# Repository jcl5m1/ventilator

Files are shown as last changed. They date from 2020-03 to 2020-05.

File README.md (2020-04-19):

Last updated 2020/04/19

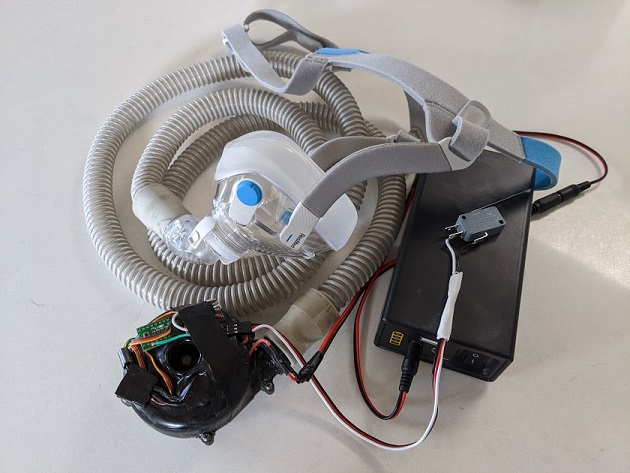
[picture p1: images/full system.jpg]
Full System


# Low-Cost Open-Source Ventilator-ish Device or PAPR

NOTE: This is currently an independent project not affiliated with any commercial institution.

* In the event that COVID-19 hospitalizations exhaust the availability of FDA approved ventilators.  This project documents the process of converting a low-cost CPAP (Continuous Positive Airway Pressure) blower into a rudimentary non-invasive pressure support ventilator that could help with breathing during respiratory distress.  It's an evolving project, but in it's current form, it most aligned with the definition of a non-invasive pressure support BiPAP ventilator.
 * This same project can also be used to create a reasonable [low-cost Powered Air Purifying Respirator (PAPR)](https://github.com/jcl5m1/ventilator/wiki/Build-a-Low-Cost-PAPR) with filter adapter and mask.  PAPRs are effective pieces of Personal Protective Equipment (PPE) that could be helpful to caregivers. PAPRs will also be in extremely short supply and are much less risky and controversial than a DIY ventilator.  You may be able to save many more lives by building a PAPR that protects a caregiver than a mediocre ventilator for one patient.  Unless you are able to participate in the detailed engineering and medical discussions regarding mitigating the risks of high pressure ventilation, I would highly recommend focusing on the PAPR version of this build.

### WARNING/DISCLAIMER: Whenever possible, please seek professional medical care with proper equipment setup by trained individuals. Do not use random information you found on the internet. I am not a medical professional, just a random person putting information on the internet. There are significant risks associated with using a high pressure BiPAP as a DIY ventilator without medical supervision.  

### What are the primary risks of a DIY ventilator?
 * Being viewed as a viable alternative to available professional care or delaying seeking professional care.  This should be viewed as an educational resource or a last resort option only.  Community driven engineering efforts like this run the risk of making it "too easy to be harmful" which would be a bad outcome.
 * Using non-invasive interfaces (such as masks and mouth pieces) can create aerosolized virus infecting many others in clean environments.  Infecing yourself or other healthy individuals multiplies the problem.  Usage should be restricted to places where aerosolized viruses are already abundant (lots of unmasked symptomatic individuals), COVID wards, or in isolation. <strong>NOTE: Self-quarantine in an apartment or multi-unit residence is NOT proper isolation due to potential shared ventilation and sewage.</strong>
* Giving too high a pressure (such as 20cmh2o and up) without observing lung compliance can cause rupture of infected lung tissue.  This design currently lacks several features that provide enough feedback to a caregiver to monitor that risk.
* See [more detailed discussion of these risks and potential engineering/administrative controls to address them](https://github.com/jcl5m1/ventilator/wiki/Notes-from-chatting-with-a-pulmonologist).

### Too risky? Build a low-cost PAPR!
One more time, a [low-cost Powered Air Purifying Respirator (PAPR)](https://github.com/jcl5m1/ventilator/wiki/Build-a-Low-Cost-PAPR) is highly valuable for caregivers, and may have much more positive impact than bulding a mediocre ventilator.

### Want to build something without electronics?  Consider building PPE
* There are many efforts making [DIY face shields](https://www.google.com/search?q=3d+printed+face+shields)
* There are many efforts making [face masks](https://www.google.com/search?q=make%20a%20face%20mask) from home materials.  We've also posted some of [our results of testing filter performance of different materials.](https://github.com/jcl5m1/ventilator/wiki/Material-Filter-Testing)

### Hardware Requirements and Medical/Government Request for proposals:
 * Requirements doc from [Code Life Ventilator Challenge - Montreal General Hospital Foundation](https://www.agorize.com/en/challenges/code-life-challenge/pages/guidelines?lang=en) (Canada)

 * Requirements from [Gov.UK  - Rapidly Manufactured Ventilator System](https://www.gov.uk/government/publications/coronavirus-covid-19-ventilator-supply-specification/rapidly-manufactured-ventilator-system-specification?fbclid=IwAR2IgOyENgHJTsLouIiikpuiwgwupdB8d8Aun2he8nzMPWGfhBVhaG_sMqo) (UK)

### Current Hardware Capabilities
  * This rudimentary design can have a programmable breathing rate (ex: 10-16/min)
  * It can have a programmed Positive End-Expiratory Pressure (PEEP)
  * The blower is physicially able to hit a peak airway pressure of up to 45cmh2o. However, <strong>[going above 20cmh2o can be DANGEROUS](https://github.com/jcl5m1/ventilator/wiki/Notes-from-chatting-with-a-pulmonologist)</strong>.  
  * It cannot yet hit a target tidal volume.  What level of accuracy in volume would be sufficient?  100mL? 10mL?  
  * It does not regulate fractional oxygen (FiO2).  But, a down stream connection to an O2 tank is possible to boost O2 concentration with manual flow adjustment.  I could use a pointer to a low cost O2 sensor.
  * It is lacking in many other ways, but it is possible that this limited functionality could be helpful when better care is not available.  It is also a starting point for making progress.  Critical features can be added over time.

Here's a youtube video walking through the components as of 2020/03/17:
Youtube video (https://www.youtube.com/watch?v=n57u1NvXBgw)

There are also many other efforts in this direction.  [Here's a short list of them](https://github.com/jcl5m1/ventilator/blob/master/resources.md) Thanks! [discussion](https://github.com/jcl5m1/ventilator/pull/20) 

# To Do's - aka Things I could use help with

I've moved the [To Do's to a Wiki](https://github.com/jcl5m1/ventilator/wiki/TaskList) so it is easier to update. Please check there if you are interested in helping.  Thanks to those that already have!

To provide comments/feedback/offer help, [create a new issue](https://github.com/jcl5m1/ventilator/issues) on the project.  Thanks!

# Useful References/Docs about the supply shortages, and guidance around unapproved devices:

There is a growing list of useful documents around guidance for use of unapproved equipment, and information around estimated shortages of both ventilators and personal protective equipment.  We have moved them to [References Wiki to enable better updates](https://github.com/jcl5m1/ventilator/wiki/Useful-References) to make it easier to maintain.

# Materials
1. [Continuous Positive Airway Pressure (CPAP)](https://en.wikipedia.org/wiki/Continuous_positive_airway_pressure) devices are commonly used by individuals to treat [sleep apnea](https://en.wikipedia.org/wiki/Sleep_apnea). As a result, CPAP blower components are fairly abundant. Used ones are available on eBay and new ones on Alibaba. In many of these devices, the blower is a simple BLDC motor that can be driven with an Electronics Speed Controller (ESC) used by quadrotors and RC cars.  The one I used is pulled from a [Respironics REMStar](https://www.google.com/search?q=respironics+remstar&safe=off&rlz=1C1CHBF_enUS809US809&sxsrf=ALeKk00Uw98vXCAyCiiSglgt-2Ucnz5RCg:1584357572342&source=lnms&tbm=isch&sa=X&ved=2ahUKEwj2mq_y757oAhXOvJ4KHV22D1EQ_AUoAnoECAwQBA).  In volume, these blower components can be under $20.  
  * Alternative: test a [12v inflator pump](https://www.amazon.com/gp/product/B013UQ0T2Y/ref=ppx_yo_dt_b_asin_title_o01_s00?ie=UTF8&psc=1) which is even more abundant.  
  * Alternative: [print a blower](https://drmrehorst.blogspot.com/2018/04/the-mother-of-all-print-cooling-fans.html) [[discussion]](https://github.com/jcl5m1/ventilator/issues/8)

2.  [Arduino Compatible Nano/Clone](https://www.amazon.com/s?k=Arduino+nano) to control the motor speed, breathing cycles, and handle user input.   Download the [Arduino IDE](https://www.arduino.cc/en/main/software) to program the [microcontroller software](https://github.com/jcl5m1/ventilator/tree/master/ventilator_control).

3. Brushless DC Motor [Electronic Speed Controller](https://www.amazon.com/Hobbypower-Brushless-Controller-Multicopter-Helicopter/dp/B00XKX5TBE/ref=sr_1_17?keywords=12v+ESC&qid=1584357758&sr=8-17) capable of at least 10A. 

4. Button or switch for input control.  The code cycles through 5 levels of pressure. Double click to switch between CPAP and BiPAP/Fixed PEEP mode.

5. 12v DC power supply that can handle at least 5A.  The blower works pretty hard, and the breathing cycles can create voltage drops which will reset the Arduino if the supply is not strong enough.

6. Tubing and face mask.  If you search for [CPAP face mask](https://www.google.com/search?q=cpap+mask), you'll find many options/suppliers.  A full face mask that covers both the mouth and nose will enable pressure buildup in the lungs.  As an alternative, see below for draft 3D printable parts.

7. Optional [inline 12v battery backup](https://www.amazon.com/gp/product/B07H8F5HYJ/ref=ppx_yo_dt_b_search_asin_title?ie=UTF8&psc=1).

# Building
This is the full system with mask, tubing, pump, 12v battery, and switch for input.  However, I would strongly recommend running this with a DC power supply since the battery will only last about 3-4 hours.  <strong>Wearing the mask with a dead battery could cause dangerous CO2 build up.</strong>  This [particular battery](https://www.amazon.com/gp/product/B07H8F5HYJ/ref=ppx_yo_dt_b_search_asin_title?ie=UTF8&psc=1) can charge and supply power at the same time, acting as an inline battery backup to wall power.

Full System

Below is a close up of the extracted blower.  It is simply a BLDC motor driving a blower fan.  A small ESC and Arduino are attached (technically a Teensy2.0++, but the code has now been changed to an Arduino Nano).  It has a 3d printed tapered hose adpater on it to fit in the hose.  The [microcontroller software](https://github.com/jcl5m1/ventilator/tree/master/ventilator_control) can be programmed with the [Arduino IDE](https://www.arduino.cc/en/main/software). The software goes through a short initialization sequence to configure the ESC; it then starts at the lowest CPAP setting.  You can use the switch to cycle through pressure levels, and double click to cycle through operating modes.

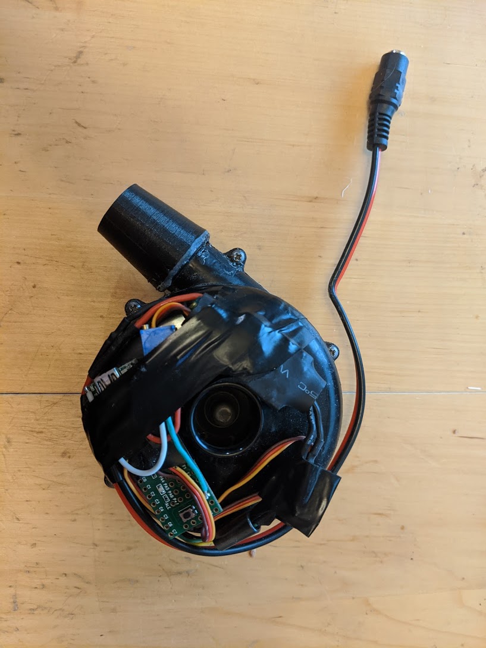
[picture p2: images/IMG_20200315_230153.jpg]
Extracted CPAP Blower


Here is the schematic for the electronics. As you can see, it is very simple with only a few parts.  A slightly modifed version that is able to [sense the blower current is here](https://github.com/jcl5m1/ventilator/wiki/Breathing-Back-Pressure-Data-Analysis).
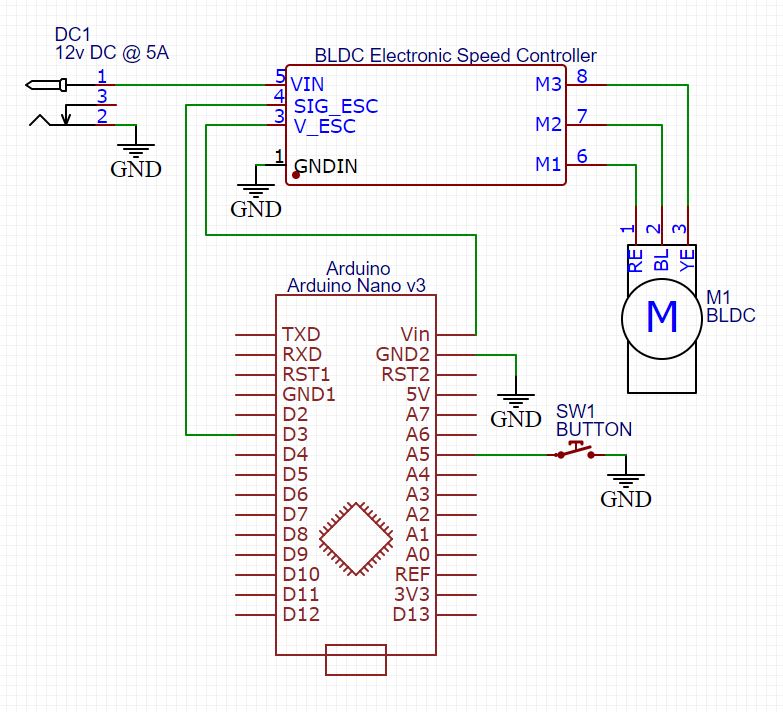
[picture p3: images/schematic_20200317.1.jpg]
schematic


## Face mask / Tube Adapter
Since I have a CPAP, I happen to have a [Resmed AitFit F20](https://www.amazon.com/Resmed-AirFit-Frame-System-Cushion/dp/B07C9MR5RS) mask that I can use.  This is quite comfortable and covers both the nose and mouth to make a good seal.  However, if you can't get a mask,  below is a prototype mouthguard that fits in the category of not-so-great-but-usable-if-you-have-a-lot-of-tape.  I am using some [elastic straps](https://www.amazon.com/gp/product/B07WZRZDPF/ref=ppx_yo_dt_b_search_asin_title?ie=UTF8&psc=1) as head gear.  However, in order to get a good air seal to get enough positive pressure, this would require some tape.  A little bit of leakage is actually desirable to allow CO2 to escape near the mouth and nose to flush out the air over time; this prevents CO2 from being stuck in the tube.  <strong>WARNING: wearing this sealed to the mouth with tape without power may cause dangerous CO2 build up.</strong>

Download the [[3D model]](https://github.com/jcl5m1/ventilator/blob/master/3dmodels/mouthgaurd_v20200316.2.stl) [[Fusion 360 link]](https://a360.co/33rwb1R).

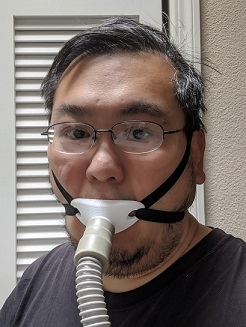
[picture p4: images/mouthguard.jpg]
Mouth Guard

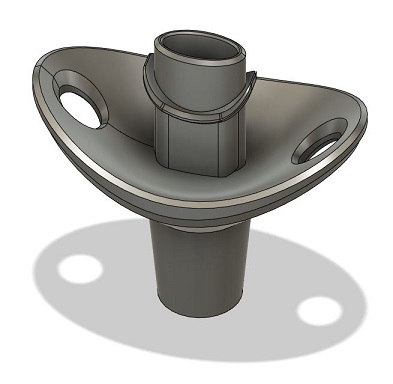
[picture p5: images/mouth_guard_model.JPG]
Mouth Guard model


# Pressure Testing

This is a picture of my test rig to measure the output pressure.  It is a U-shaped tube with an attached measuring tape to check displacement of water.  The actual liquid displacement is 2x the measured line since liquid is being pushed downwards an equal amount on the other side of the U, doubling the displacement. (I think this is the correct way to measure).  At full blast at 12v, it is achieving 45cmh2o. <strong>[WARNING: Going above 20cmh2o can be DANGEROUS](https://github.com/jcl5m1/ventilator/wiki/Notes-from-chatting-with-a-pulmonologist)</strong>.  So, these blowers are plently powerful.

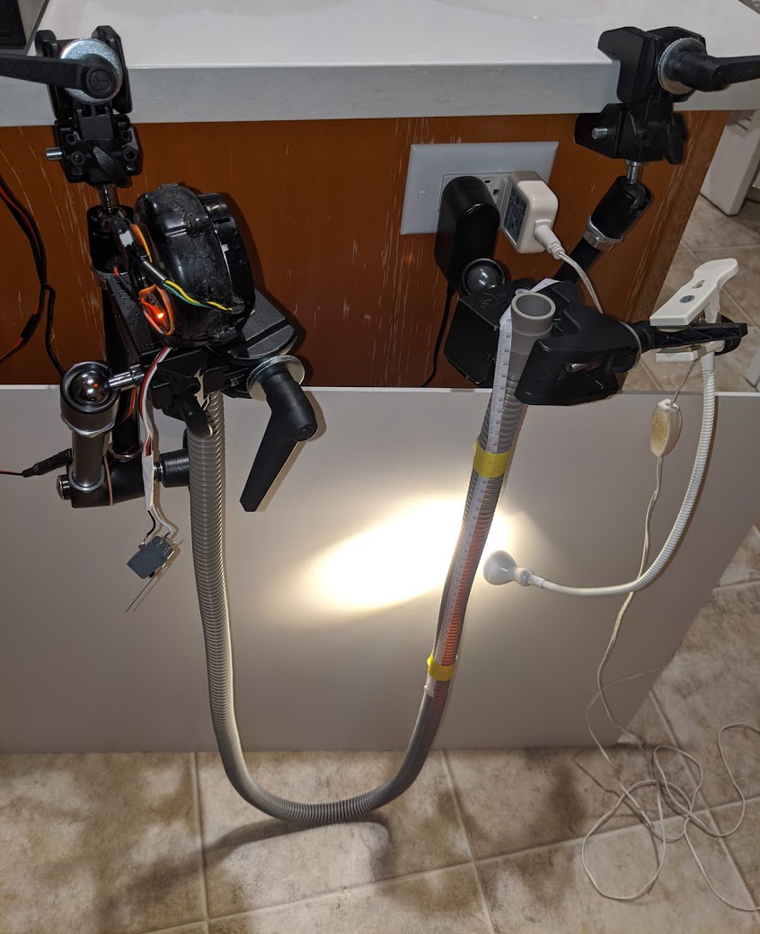
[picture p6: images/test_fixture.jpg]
Pressure measurement fixture


Here are some images showing the dislacement of the liquid at different speeds.  I happen to have Diet Dr. Pepper on hand which makes it easier to see the liquid level rather than just plain water.

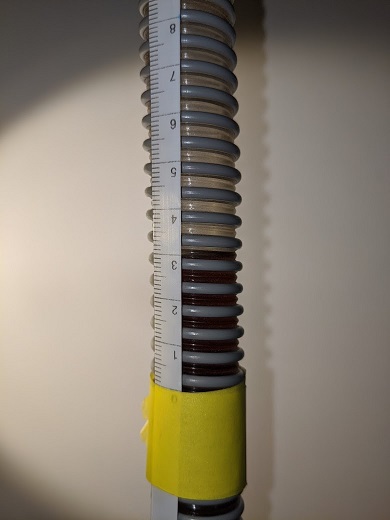
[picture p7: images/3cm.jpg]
3cm
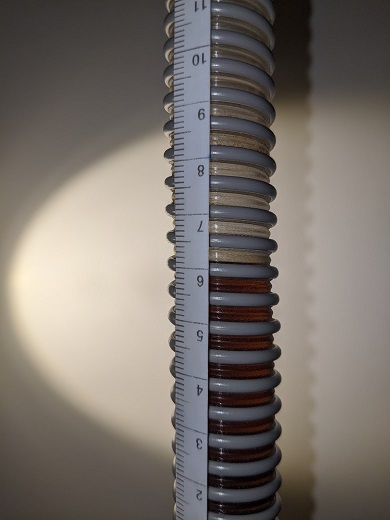
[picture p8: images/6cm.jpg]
6cm
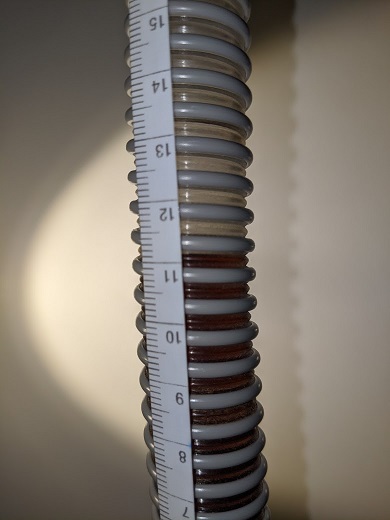
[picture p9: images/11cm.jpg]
11cm
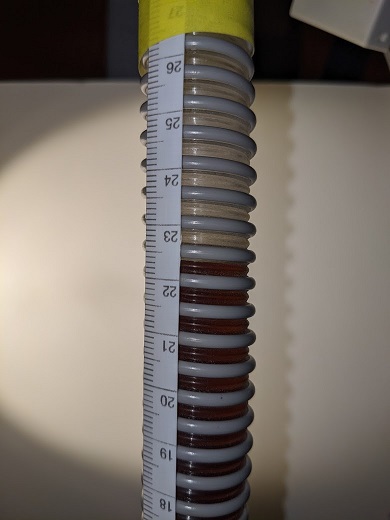
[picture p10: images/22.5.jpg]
22.5cm
   

Here's a [video of the blower pushing a breathing cycle of 16 cycles/min oscilating between 12 and 22cmh2o](https://photos.app.goo.gl/b3yMPE5QpdeduxKS6).

# Air Filtration - PAPR Option

An open air blower into someone's airway isn't great.  If possible, some filtration is preferred.  These parts were originally used for a DIY [Powered Air Purifying Respriator (PAPR)](https://en.wikipedia.org/wiki/Powered_air-purifying_respirator). However, adding a filter will definitely affect the output pressure.  It will depend on the blower you have if the motor can handle the additional load.  Given the headroom of the blower I tested, these CPAP blowers can probably handle the filter and still hit the target pressure.  However, I haven't done long term thermal testing at high pressure and with a strong filter. These adapter plates can be attached with liberal amounts of hot glue and wrapping the unit in vinyl tape to get a reasonably airtight seal.  My blower's enclosure was not air-tight, so it is difficult to guarantee that 100% of the air is coming only through the filter.  Setting the blower to a low CPAP pressure, and leaving the face mask vent holes open will allow it to function reasonably as a PAPR.

* This is an adapter plate for a [3M P100 or N95 face mask filter cartridge](https://www.amazon.com/3M-50051138464658-Cartridge-Filter-Organic/dp/B07571LR2K/ref=sr_1_2?crid=36AKE548EW15U&keywords=3m+p100+cartridge&qid=1584418326&sprefix=3m+p100+cartrige%2Caps%2C202&sr=8-2). Download [[3D model]](https://github.com/jcl5m1/ventilator/blob/master/3dmodels/3M_filter_adapter.stl) [[Fusion 360 link]](https://a360.co/2QnQQOU)

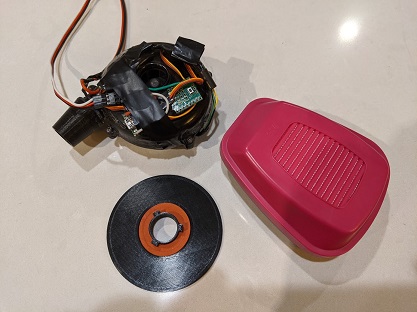
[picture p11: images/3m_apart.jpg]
3M Apart
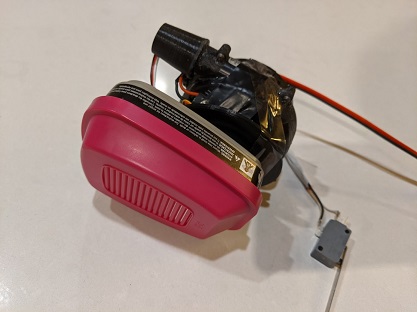
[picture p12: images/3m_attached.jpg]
3M attached
 

* This is an adapter plate for a [NATO 40mm gas mask filter cartridge](https://www.amazon.com/MIRA-Cartridge-Respiratory-Protection-Filter/dp/B07L38TYSF/ref=sr_1_2?keywords=40mm+gas+mask+filters&qid=1584418565&sr=8-2).  These fitlers are available with [CBRN](https://en.wikipedia.org/wiki/CBRN_defense) ratings which are needed for viral and bacterial defense similar to those [approved by the CDC/NIOSH](https://www.cdc.gov/niosh/npptl/standardsdev/cbrn/papr/default.html). Download [[3D model]](https://github.com/jcl5m1/ventilator/blob/master/3dmodels/NATO_40mm_adapter.stl) [[Fusion 360 link]](https://a360.co/3914gXs)

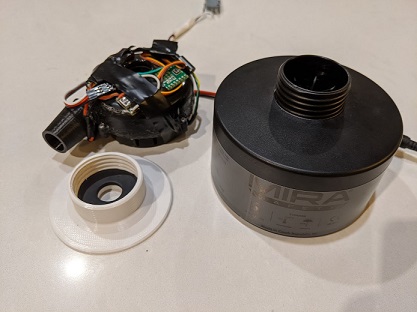
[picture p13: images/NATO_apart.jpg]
NATO Apart
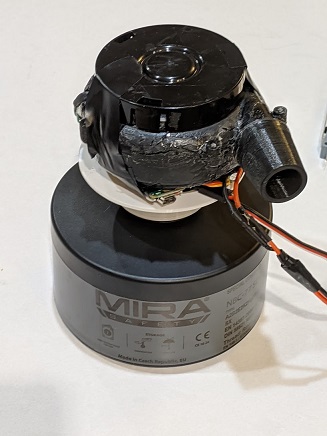
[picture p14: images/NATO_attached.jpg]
NATO attached
 

* This is an option for an [inline filter](https://www.directhomemedical.com/cart/merchant.mvc?Screen=PROD&Product_Code=1-H1605-inline-bacterial-viral-cpap-filters&Store_Code=DHM&gclid=EAIaIQobChMIo-G35omi6AIVSrzACh29hwv3EAQYASABEgK9FPD_BwE) [[discussion]](https://github.com/jcl5m1/ventilator/issues/4) that looks easy to install, and would be helpful for non-CPAP blowers. 

# Update Log

Click [here](https://github.com/jcl5m1/ventilator/wiki) to see updates.

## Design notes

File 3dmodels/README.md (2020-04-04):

# 3D models 

## Requirements & recommendations

**Supported file formats**

- STL - for 3D printed models
- STEP - for objects representing part to be used as a reference
- Application specific projects (like SolidWorks, Fusion360) - CAD formats other users could edit 

**Unsupported file formats**
- Mesh-based objects (.obj, .3dmax, etc) - these formats are not editable by CAD software and should be avoided.

**3D printing recommendations:**

1. Part dimensions should be within 200x200x200mm - print area limits for most 3D printers
2. Avoid overhangs - parts should be printable without Support
3. For bigger parts please also try to provide stacked version - i.e. parts on top of each other, so we could print them in bulk
4. Recommended print settings should be provided for printing with PET-G (material accepted for medical purposes)

# Reference sheet on original parts

## CPAP filter
Please check Wiki page for more details: https://github.com/jcl5m1/ventilator/wiki/Bacterial-Viral-Filter-for-CPAP-Machines

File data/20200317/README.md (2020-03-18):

# Dataset explaination:

Data rows are printed from the Arduino at approximately 100Hz (minus serial port overhead, and few if statements).
Filename format is A_B_C.csv with parts defined below

A: as follows:
 * cpap - constant pressure
 * bipap - two pressure cycle at 16 cycles/min

B: spdX where X approximately maps to:
 * 60 ~= 10cm/H20
 * 90 ~= 18cm/H20
 * 120 ~= 32cm/H20

C: as follows:
 * open - not in mouth
 * breathing - in mouth, breathing
 * breathing_sync - in mouth, breathing in sync with blower cycle
 * breathing_async - in mouth, breathing out of sync with blower cycle

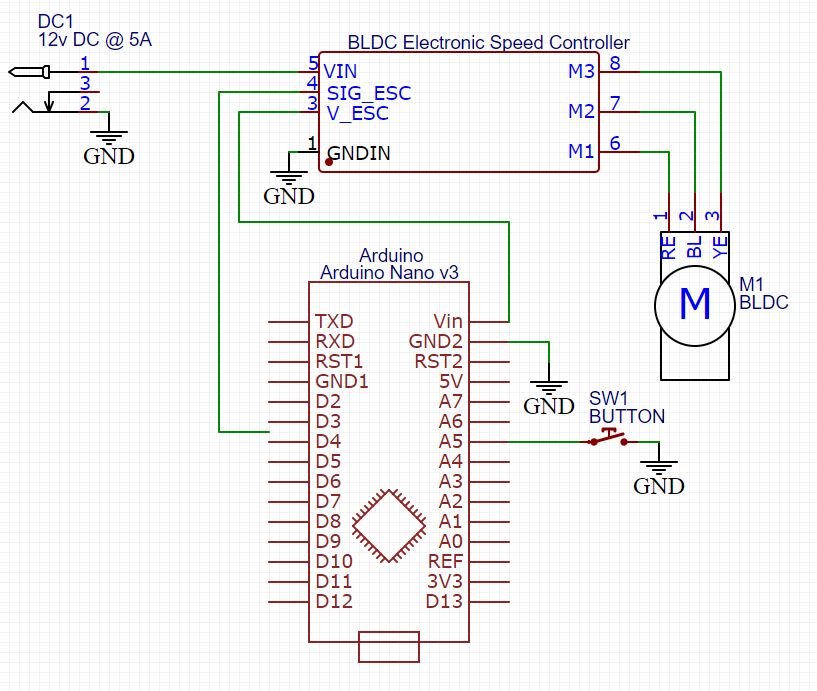
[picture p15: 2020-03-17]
images/schematic_20200317.0.jpg

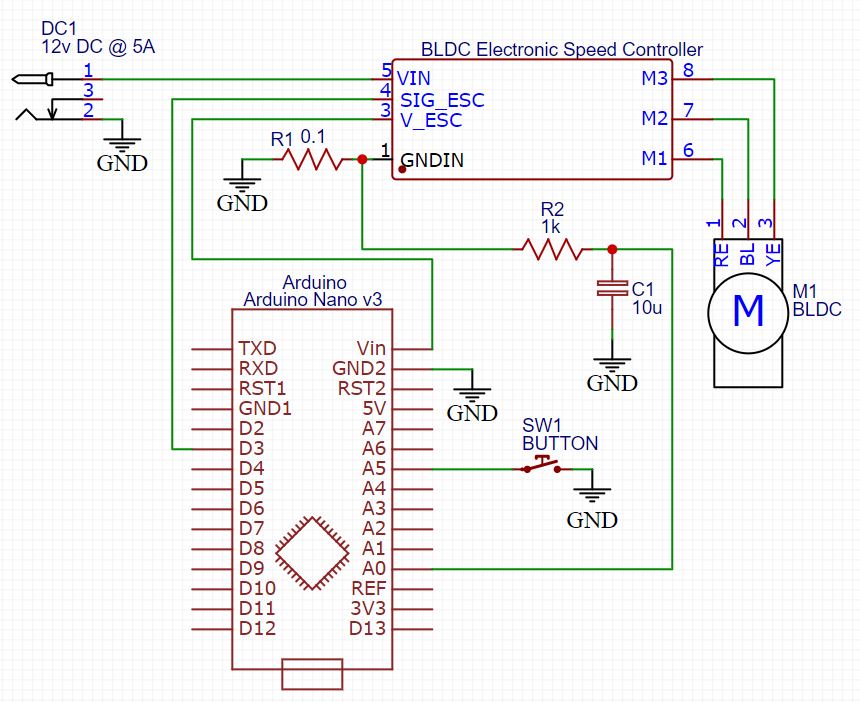
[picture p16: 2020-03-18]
images/schematic_20200317.2.jpg

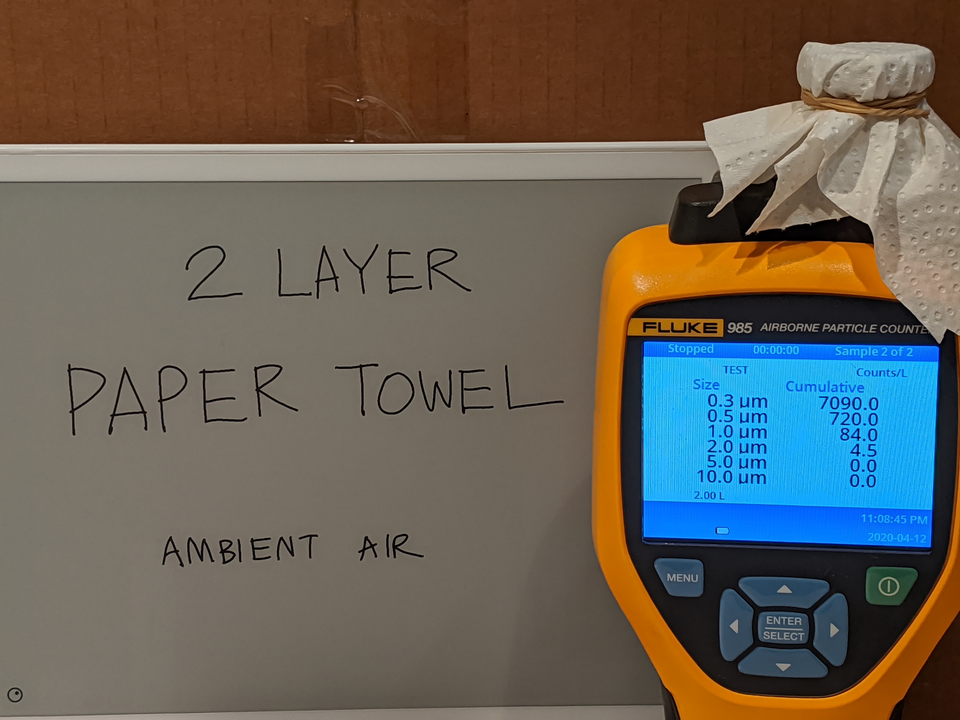
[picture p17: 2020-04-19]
images/filter_images/measuring paper towel 2 layers.jpg

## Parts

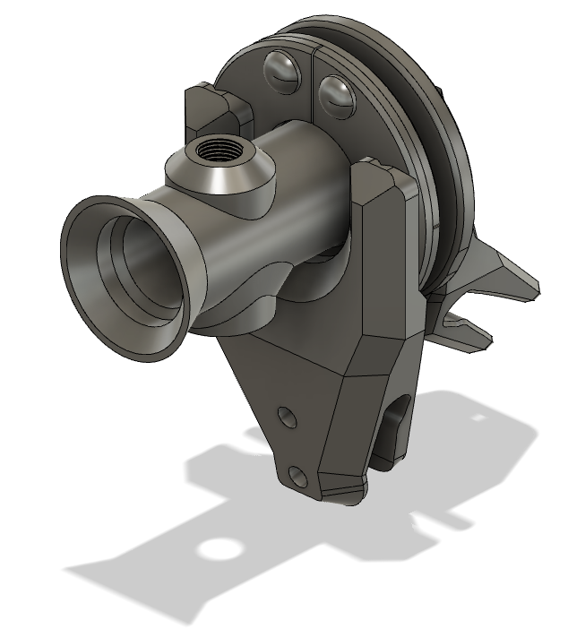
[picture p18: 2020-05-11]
images/breathability/breathability_3D_parts.png

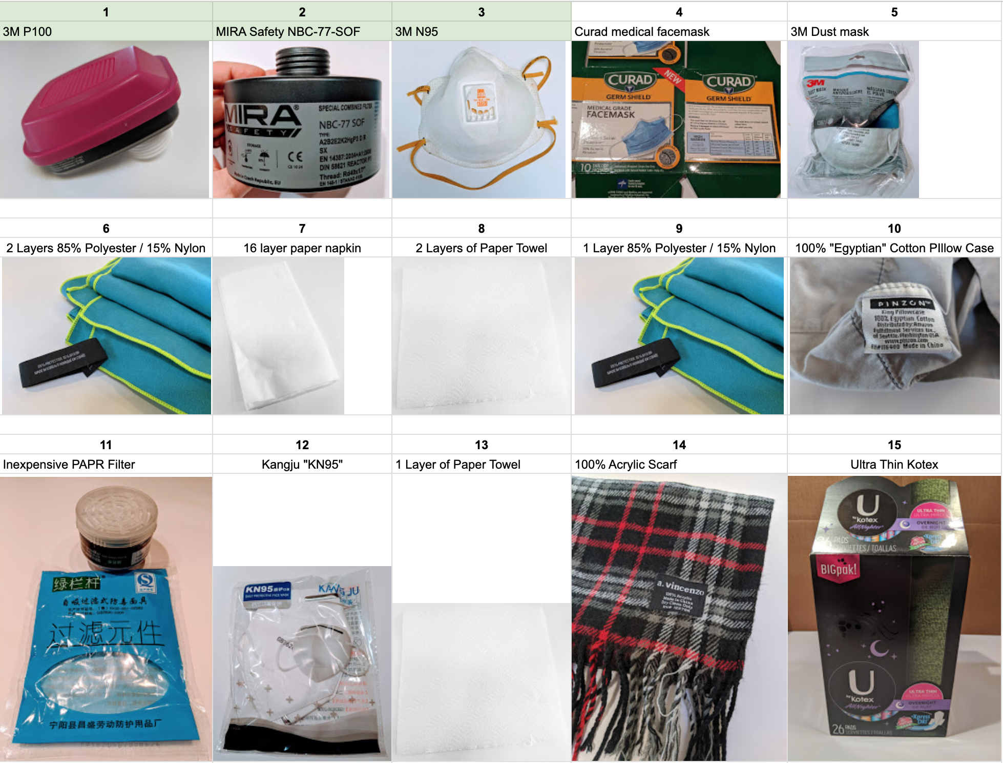
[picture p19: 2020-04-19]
images/filter_images/Materials table.png

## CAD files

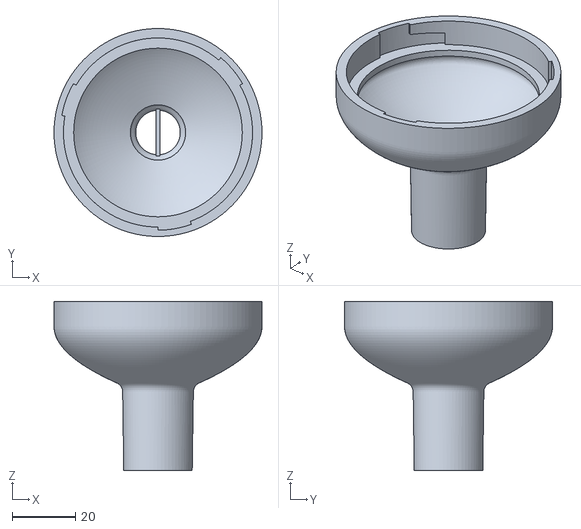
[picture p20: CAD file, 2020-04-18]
3dmodels/CPAP_outlet_filter_Lower_part.stl
66.0 x 66.0 x 53.7

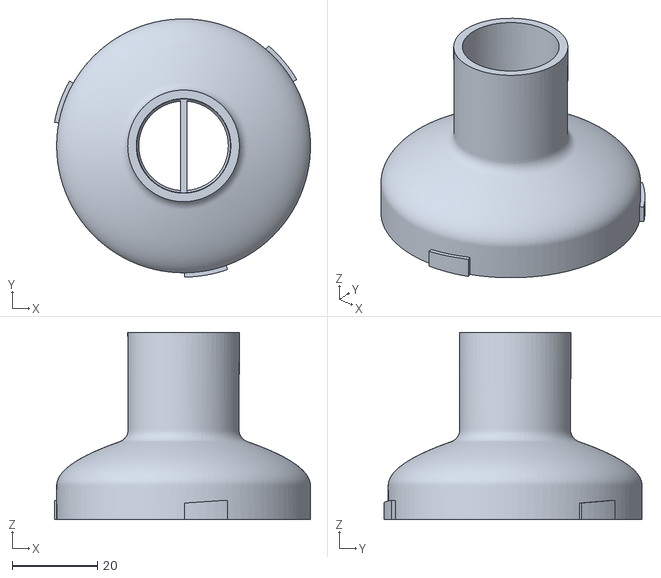
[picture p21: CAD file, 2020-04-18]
3dmodels/CPAP_outlet_filter_Upper_part.stl
60.1 x 60.6 x 44.0

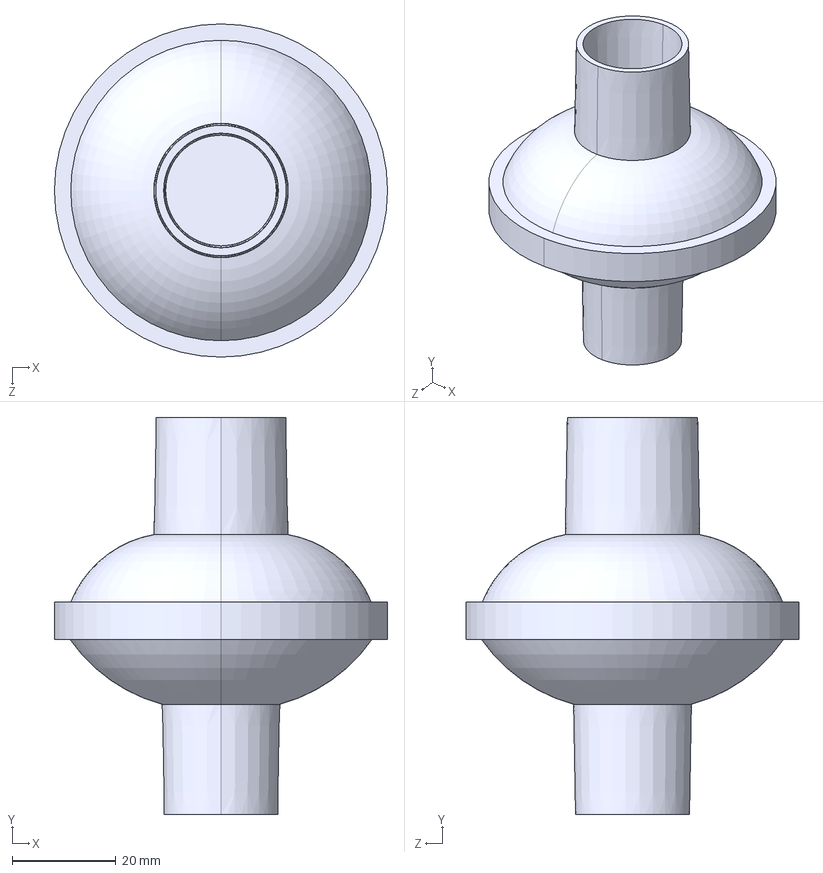
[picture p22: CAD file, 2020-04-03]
3dmodels/Inline_filter_VB-65mm.STEP
64.3 x 76.6 x 64.3 mm

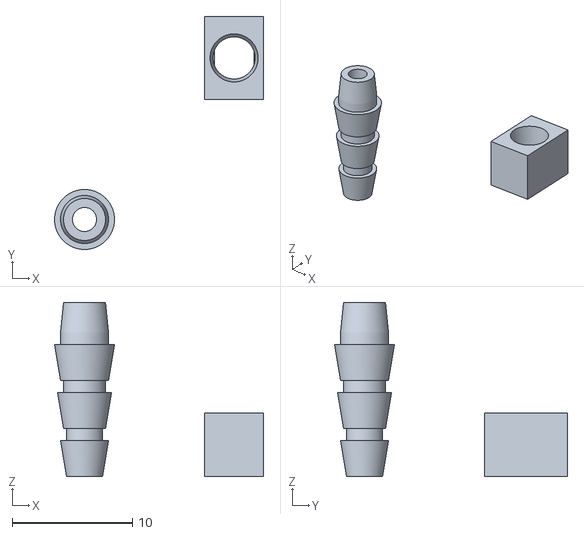
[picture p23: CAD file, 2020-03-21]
3dmodels/MS3611PressureCoupling1_0.stl
17.4 x 19.4 x 14.5

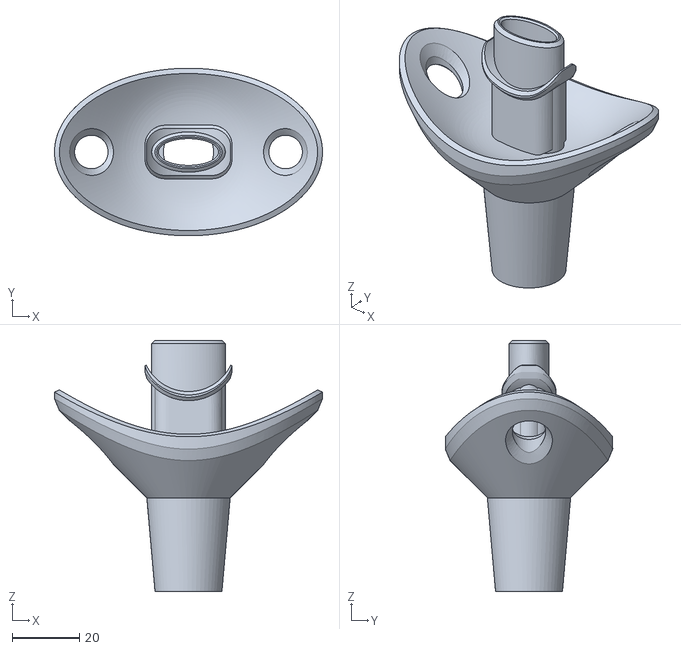
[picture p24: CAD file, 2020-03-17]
3dmodels/mouthgaurd_v20200316.2.stl
80.0 x 50.0 x 75.0

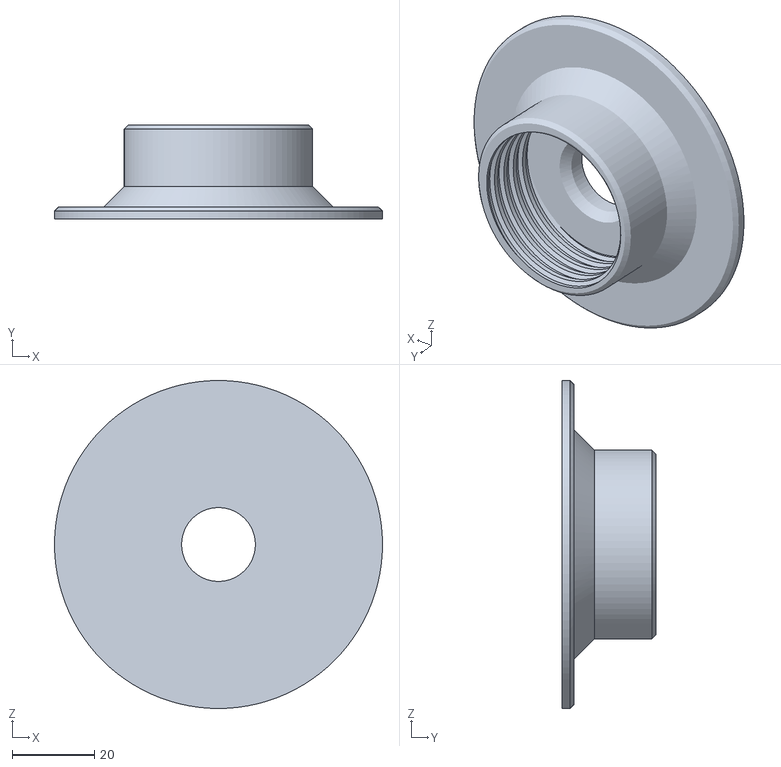
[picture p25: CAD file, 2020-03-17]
3dmodels/NATO_40mm_adapter.stl
80.0 x 23.0 x 80.0

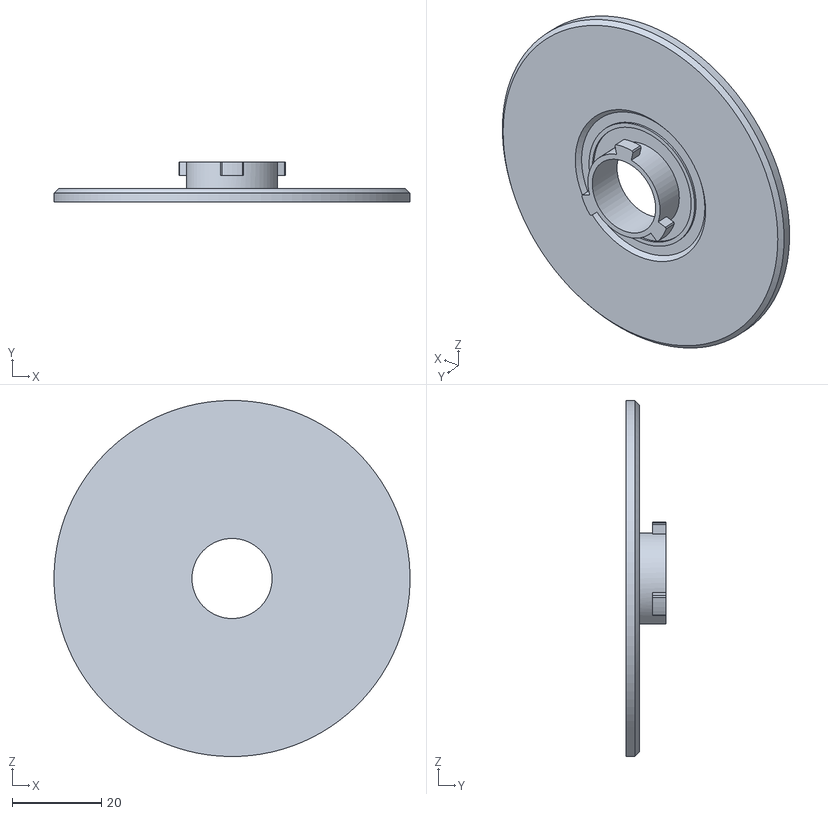
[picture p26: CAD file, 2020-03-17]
3dmodels/3M_filter_adapter.stl
80.0 x 9.00 x 80.0

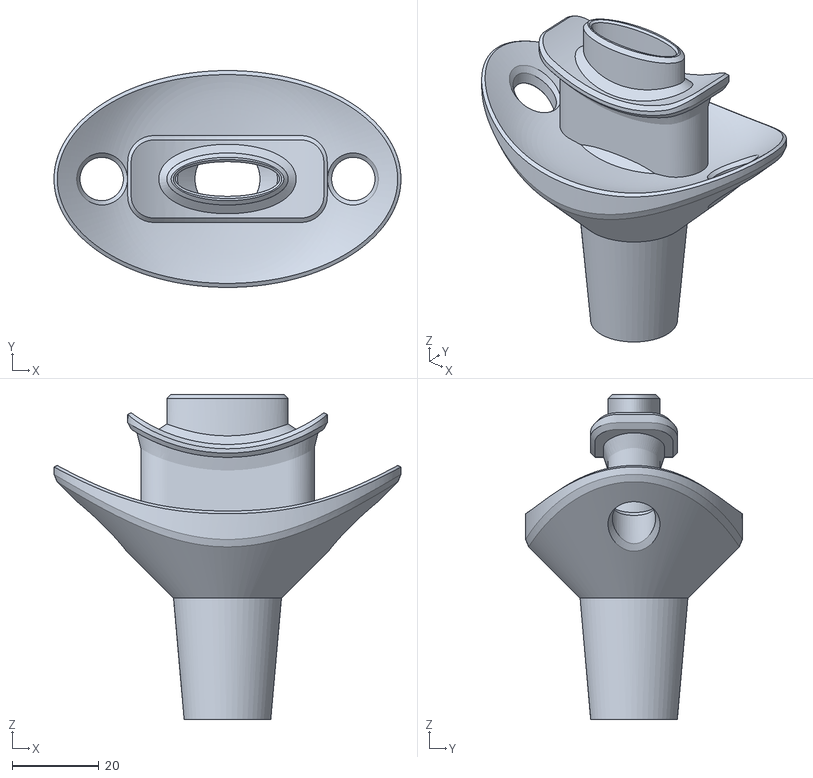
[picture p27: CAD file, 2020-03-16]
3dmodels/mouthgaurd_v20200316.1.stl
80.0 x 50.0 x 75.0

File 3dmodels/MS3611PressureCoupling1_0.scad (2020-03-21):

//Pressure sensor tube adapter
//Version 1.0
//March 20, 2020
/* Designed to fit 
//     * over the top of an MEAS MS5611 pressure sensor
//     * connect to a 3-7mm ID flexible tubing 
 MEAS MS5611 specifications are available at https://www.te.com/commerce/DocumentDelivery/DDEController?Action=showdoc&DocId=Data+Sheet%7FMS5611-01BA03%7FB3%7Fpdf%7FEnglish%7FENG_DS_MS5611-01BA03_B3.pdf%7FCAT-BLPS0036 
*/

/*

Copyright 2020 Alex Bobotek

    This program is free software: you can redistribute it and/or modify
    it under the terms of the GNU General Public License as published by
    the Free Software Foundation, either version 3 of the License, or
    (at your option) any later version.

    This program is distributed in the hope that it will be useful,
    but WITHOUT ANY WARRANTY; without even the implied warranty of
    MERCHANTABILITY or FITNESS FOR A PARTICULAR PURPOSE.  See the
    GNU General Public License for more details.

    You should have received a copy of the GNU General Public License
    along with this program.  If not, see <https://www.gnu.org/licenses/>.
*/


//MS5611 dimensions
MSwidth=3;
MSlen=5;
MSh=1.8;

MSgap=0.15;
MShoodThick=.8;
MSheadroom=1;       // free room over sensor inside hood
MSceilingThick=2.5;

barbID=2;
barbLen=15;
barbMinOD=3;
barbMaxOD=7.5;
barbMaxTaper=4;
barbMinTaper=3.5;
barbTaperLen=MSceilingThick+1.5;
taperSlope=1/3; // ratio of diameter change to height change
taperZ=3;
neckZ=1;


translate([10,10,0]) block();
barb();

module block() {
    difference() {
        cube([MSwidth+2*MSgap+2*MShoodThick,MSlen+2*MSgap+2*MShoodThick,MSh+MSheadroom+MSceilingThick]); // Outer shell
        translate([MShoodThick,MShoodThick,0]) cube([MSwidth+2*MSgap,MSlen+2*MSgap,MSh+MSheadroom]);    // Inner cavity
        translate([MSwidth/2+MSgap+MShoodThick,MSlen/2+MSgap+MShoodThick,MSh+MSheadroom]) 
            cylinder(d1=barbMinTaper,d2=barbMaxTaper,h=MSceilingThick, $fn=72);    // Tapered socket
        //translate([MSwidth/2+MSgap+MShoodThick,MSlen/2+MSgap+MShoodThick,0])
            //cylinder(d=barbID,h=MSh+MSheadroom+MSceilingThick, $fn=24);
    }
};
    


module  ring(minD,ringH) {
    cylinder(d1=minD,d2=minD+ringH*taperSlope,h=ringH,$fn=72);
    translate([0,0,ringH]) cylinder(d=minD,h=neckZ,$fn=72);
}

module barb(){
    difference() {
        union() {
            translate([0,0,3*(taperZ+neckZ)]) cylinder(d2=barbMinTaper,d1=barbMaxTaper,h=MSceilingThick, $fn=72);    // Tapered socket
            translate([0,0,2*(taperZ+neckZ)]) ring(minD=4,ringH=3);
            translate([0,0,1*(taperZ+neckZ)]) ring(minD=3.5,ringH=3);
            translate([0,0,0*(taperZ+neckZ)]) ring(minD=3,ringH=3);
        }
        cylinder(d=barbID,h=4*(taperZ+neckZ),$fn=72);
    }
}

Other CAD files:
3dmodels/ventilator_filter_CPAP.f3d

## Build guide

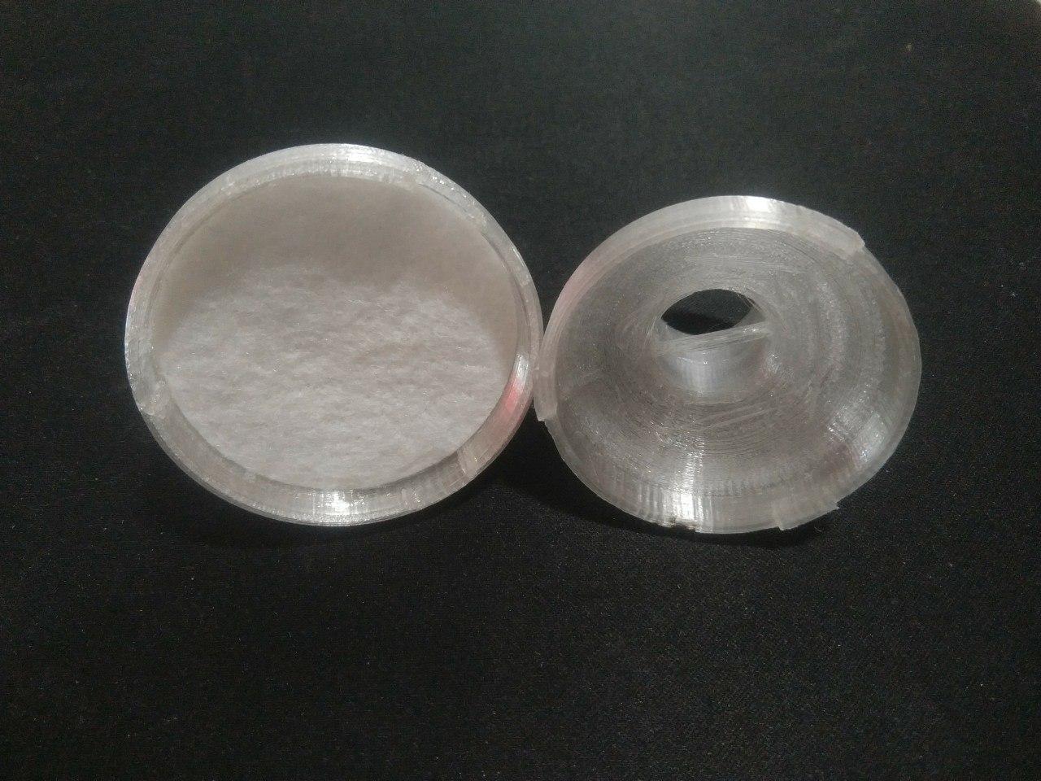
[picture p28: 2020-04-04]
3dmodels/images/CPAP-3D-printed-filter-opened.jpg

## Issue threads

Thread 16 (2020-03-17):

jcl5m1/ventilator #16: Professional Insight?

aris-t, 2020-03-17:
So I hit up a friend with connections to people who actually make ventilators and these are some areas of concern they brought up.

- "This seems like a very very dangerous endeavor"
- Inflating patient’s lungs correctly (including being in sync with their respiratory drive) 
- Weaning the patient off support later is a super complex thing with no room for error. 
         Though I believe this really only becomes an issue after ~24 - 72 hrs of use, (Needs confirmation)
- They also pointed out that this wouldn't be a true ventilator as you usually sedate and intubate patients in that case.
- They were also concerned with the potential for the positive pressure gas exiting  the patient to contain aerosolized virus.

mrquincle, 2020-03-17:
What's their suggestion? Can they open source their hardware? Can they ramp up their production enough? Can they under FDA have other companies helping them to ramp up?

peteflorence, 2020-03-18:
### Re: project comparison with other projects
1. The ideal scenario would be to ramp production of FDA approved ventilators.
2. There are parallel efforts to this project to do exactly that.
3. Given the possibility that these efforts might not meet global demand, then we should explore low cost, easy-to-manufacture ventilator options.  Keep in mind this will be a global need, not just for privileged countries like the U.S., etc.
4. Parallel to this project, there are other low cost open source projects as well.

Given the importance of each day, some level of parallel efforts seem great.

### Re: technical questions
1. Regarding intubation with an endotracheal tube -- could somebody point to if we know that COVID patients actually need an endotracheal tube?  This overview on ventilators (https://www.youtube.com/watch?v=gk_Qf-JAL84) points out that there are two different use cases for ventilators.  One (1) is that the patient can't protect liquids and solids from going down the trachea.  Two (2) is that they can't breathe on their own.  If the requirement is only for (2), it seems possible that an endotracheal tube is not required.  Need doctor to advise.
2. If an endotracheal tube is needed, it could be added to the design.
3. "They were also concerned with the potential for the positive pressure gas exiting the patient to contain aerosolized virus." -- yes, need to make sure this is solved for and tested.
4. "Inflating patient’s lungs correctly (including being in sync with their respiratory drive)" -- it depends on the mode of operation of the ventilator.  If the patient initiates the breath, then yes the event of the patient starting to inhale needs to be sensed.  Note though that not all modes of operation require this.  See https://www.youtube.com/watch?v=gk_Qf-JAL84 for more.

jcl5m1, 2020-03-18:
The material I find online is very bipolar.  This person falls in the "if you don't do it right, it's a terrible idea".  The other camp, is bolting pieces of wood together to make something that might help.  There's not much middle ground of helpful information which is "in an emergency, these are really the things that matter...".

Bag-Valve Mask Ventilators don't seem to require intubation to be effective. 

If the environment already has a lot of infected patients coughing, won't there already be a lot of aerosolized virus?

When I tested it, it was very easy for me to match the rate driven by the machine.  How important is it for the machine to match the person vs the other way around?

peteflorence, 2020-03-18:
FWIW -- I am hearing from doctor friends that in severe cases, intubation is required, but not always.  Don't have data on the ratio.

fireb0lt, 2020-03-18:
Pressure support ventilators can be used with or without intubation. They can help prevent pneumonia from Covid19

Arif-I, 2020-03-18:
hi, I am from Bangladesh and following your project. The situation is going worse here and we'll def need more breathers. Even if this works with 40 or 50 % efficacy, that will be great help. I appreciate the effort of the community.

allen-munsch, 2020-03-18:
> "They were also concerned with the potential for the positive pressure gas exiting the patient to contain aerosolized virus." -- yes, need to make sure this is solved for and tested.

https://en.wikipedia.org/wiki/Venturi_scrubber

acab45, 2020-03-18:
Re: pandemic ventilator- i am not a programmer - It is my first time on github and i am a bit lost- would someone, anyone, please call me ANYTIME asap. Anthony Cabrera md, frcsc---Tel: 1-905-923-1766 OR whatsapp: 34-653-08-58-41   (34 is for Spain but i live in Hamilton, ontario, canada) OR give me your number and location and i will call you back- FYI: email: acab45@yahoo.ca
thank you
Anthony Cabrera md, frcsc

aris-t, 2020-03-18:
So i started this thread as an attempt to stir up some technical considerations which we may be overlooking but a more experienced practitioner would point out right away. I was fully expecting the response ive been getting from my more conventional contacts of "if you don't do it right, it's a terrible idea". I don't subscribe to that im much more for if you can help at all you should. Therefore im reaching out to some less conventional but more open minded contacts now.

Overall seeing @peteflorence and @jcl5m1 comments this thread seems to be serving its purpose. Keep up the good work.

rzeimer, 2020-03-18:
i suggest that providing devices that can match ventilators is not fruitful. rather we should get feedback on what are the specifications that need to be added to CPAP like machines to be useful for the cases that are not severe, which will make a large population and put pressure on the resources.
we could then use existing CPAPs which abound

allen-munsch, 2020-03-19:
Also checkout : https://gitlab.com/TrevorSmale/OSV-OpenLung

acab45, 2020-03-19:
https://www.amazon.com/Ventilator-Book-William-Owens-ebook/dp/B07D3142ZM/ref=sr_1_8?keywords=RESPIRATORY+THERAPY&qid=1584587296&sr=8-8

https://www.amazon.com/GREENS-RESPIRATORY-THERAPY-Practical-Respiratory/dp/1593309341/ref=sr_1_2?keywords=RESPIRATORY+THERAPY&qid=1584587393&sr=8-2

I AM CURIOUS IF ONE OF YOU WERE TO BUY THE BOOKS, HOW COULD YOU ALL ACCESS IT TO WORK ON IT.? IF YOU WOLD LIKE TO CALL ME BACK TO EXPLAIN PLS DO SO.

Thank you,

Anthony Cabrera
------------------------
This information is directed in confidence solely to the person named above and may contain confidential and/or privileged material. This information may not otherwise be distributed, copied or disclosed. If you have received this e-mail in error, please notify the sender immediately via a return e-mail and destroy original message. Thank you for your cooperation.

TimVanDyke, 2020-03-19:
I've been talking to acab45 and he also shared this video with me and I thought it might be a bit helpful. I think what we need to know here is basically what the use case we need to fulfill of a ventilator is, correct? 

as in, we need something along these lines (**Please correct me if I'm wrong**): 
ex:
Patient has corona virus and needs a ventilator in AC (or whatever) Mode.
they need:
- a minimum of x breaths a minute
- to monitor from u pressure to v pressure at y level precision
- alarms for a, b, and c, scenarios
- etc

acab45, 2020-03-19:
this book seems better for what you are tring to do:    open free textbook;

The Process of Breathing – Anatomy and Physiology    

 
 
 
   
The Process of Breathing – Anatomy and Physiology

acab45, 2020-03-19:
VENTILATOR PROJECT-------------i will try to find a collaborative  RT in Grand Rapids, MI)

https://www.google.com/search?q=specifications+for+a+ventialtor&oq=specifications+for+a+ventialtor&aqs=chrome..69i57j33.5460j1j7&sourceid=chrome&ie=UTF-8

https://www.sciencedirect.com/book/9780721601861/mechanical-ventilation

--->   http://www.kmscl.kerala.gov.in/ratecontractspec/Ventilator%20ICU.pdf

https://www.venteclife.com/assets/media/1064/vocsn_tech-specs_current.pdf

https://www.nxp.com/docs/en/application-note/DRM127.pdf

---------------------------------------------------------------------------------------------------------------------------------------------------------------------------

A SEPARATE BUT VERY IMPORTANT PROJECT  "facial air flow system" (very easy for you guys to design using off the shelf items, yet so critical for front line health staff in the context of "diy when supplies run out" ). I am working on the gown n hood...see images far below

i need someone who understands eletronics to design /explain how to connect a common drill battery (ie ryobi ) to a fan blower unit and along this wire have a little rehostat turn knob to adjust flow. i will send a diagram of this tomorrow. 

IMPORTANT:--->  Whatsapp for me is the best way to be able to send you all sorts of videos, images, audios, answer questions via audio back n forth  etc from my smartphone. We can setup a group on whatsap so that i can send all of you information at once then you can curate it and put it up on github as you see fit..
my whatsapp is:  

create a new message inside whatsapp :
1)-remove default canada and select SPAIN in drop down  
2)-enter 653085841 and
3)-send a test text

Thank you,

Anthony Cabrera
------------------------
This information is directed in confidence solely to the person named above and may contain confidential and/or privileged material. This information may not otherwise be distributed, copied or disclosed. If you have received this e-mail in error, please notify the sender immediately via a return e-mail and destroy original message. Thank you for your cooperation.

acab45, 2020-03-19:
https://twitter.com/charliekirk11/status/1240449295116931072?s=20

If the above is true and confirmed by other researchers, your ventilation machine may not be necessary 2 weeks from now. 
This malaria drug exists in major quanities across the USA and can be secured overnight  given the emergency powers to cut red tape by Trump decree could start tx very soon for this indcation

ac md
------------------------
This information is directed in confidence solely to the person named above and may contain confidential and/or privileged material. This information may not otherwise be distributed, copied or disclosed. If you have received this e-mail in error, please notify the sender immediately via a return e-mail and destroy original message. Thank you for your cooperation.

jcl5m1, 2020-03-19:
I had a long call with a pulmonologist yesterday.  Here are my notes:

https://github.com/jcl5m1/ventilator/wiki/Notes-from-chatting-with-a-pulmonologist

acab45, 2020-03-19:
thanks i will look at those notes you sent me.
-----------------------------------------------------------Good news. Impressive results from a study out of France showing: (excerpt:
".......At day 6 post-inclusion, 100% of patientstreated with hydroxychloroquine and azithromycin combination were virologicaly curedcomparing with 57.1% in patients treated with hydroxychloroquine only, and 12.5% in thecontrol group (p<0.001)...."
These two medications have been routinely carried in pharmacies for many years.The above was a modification from a successful study done in China many weeks ago so it seems its the real thing.
---------------------------------------At first thought, you might wonder if it is worth continuing with your project. The answer is for sure yes. If not in this country, the poorer developing countries would benefit as well as future viruses. I think world leaders have realized, that when it comes to critical aspects of healthcare, manufacturing your own (ventilators, masks etc) it is a matter of national security. I admire and am inspired by the effort of your group on Github, undaunted in the face of complexity. I really need to find you guys a RT.

Thank you,
Anthony Cabrera md, frcsc------------------------This information is directed in confidence solely to the person named above and may contain confidential and/or privileged material. This information may not otherwise be distributed, copied or disclosed. If you have received this e-mail in error, please notify the sender immediately via a return e-mail and destroy original message. Thank you for your cooperation. 

 
 

https://github.com/jcl5m1/ventilator/wiki/Notes-from-chatting-with-a-pulmonologist

acab45, 2020-03-19:
I did a quick scan of the notes, it strongly appears he is the real deal.  As you know this area of medicine is far outside my scope. I find his comments encouraging and supportive of what you are trying to do. 
ac md------------------------This information is directed in confidence solely to the person named above and may contain confidential and/or privileged material. This information may not otherwise be distributed, copied or disclosed. If you have received this e-mail in error, please notify the sender immediately via a return e-mail and destroy original message. Thank you for your cooperation. 

 
 

https://github.com/jcl5m1/ventilator/wiki/Notes-from-chatting-with-a-pulmonologist

allen-munsch, 2020-03-19:
Some techinical specifications can be found here : 

[Specification For RMVS Challenge.pdf](https://github.com/jcl5m1/ventilator/files/4355316/Specification.For.RMVS.Challenge.pdf)

acab45, 2020-03-19:
https://ca.finance.yahoo.com/news/manufacturers-offer-to-produce-medical-supplies-to-help-with-coronavirus-194049973.html

Thank you,
Anthony Cabrera------------------------This information is directed in confidence solely to the person named above and may contain confidential and/or privileged material. This information may not otherwise be distributed, copied or disclosed. If you have received this e-mail in error, please notify the sender immediately via a return e-mail and destroy original message. Thank you for your cooperation.

acab45, 2020-03-19:
It is quite possible the canadian government that is funding the ventilator manufacturing push may end up keeping it open source. I have no idea. Perhaps during the process of creating the device they might file novel patents and create a company to sell all over the world. No idea. I am not sure how intellectual property issues will pan out.

Thank you,
Anthony Cabrera------------------------This information is directed in confidence solely to the person named above and may contain confidential and/or privileged material. This information may not otherwise be distributed, copied or disclosed. If you have received this e-mail in error, please notify the sender immediately via a return e-mail and destroy original message. Thank you for your cooperation.

acab45, 2020-03-20:
A big automotive manufacterer Martinrea here in Ontario appears to be all in on ventilators
https://www.google.com/amp/s/business.financialpost.com/transportation/canadian-auto-suppliers-in-talks-to-build-ventilators-masks-during-coronavirus-crisis/amp
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

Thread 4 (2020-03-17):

jcl5m1/ventilator #4: Filtration for Intake

axjjienn, 2020-03-17:
This is a great project, and I am really excited to help. One thing I note is that it is likely we would need some kind of filter on the respirator intake, so that any kinds of allergens or other harmful particles in the environment are not transferred to the patients lungs. Just a thought.

jcl5m1, 2020-03-17:
Thanks for mentioning this.  I added a few more images and 3D files for filters I had from a precursor project.

TheAmazingJarvis, 2020-03-17:
Could it be important **where** the filter is placed? Contaminates not just from from ambient particles but particles coming form, for example, lubricants from the motor or little bits of printer filament. 

Maybe one filter at the air intake and one at the mask?

axjjienn, 2020-03-17:
I was thinking the same thing. In order to reduce parts, it makes the most sense to put the filter on the outlet of the pump. It will potentially allow contaminants to enter the pump, but I think the pumps can take it.

aris-t, 2020-03-17:
You guys may want to take a look at some of these options:
Cheap:
https://www.directhomemedical.com/cart/merchant.mvc?Screen=PROD&Product_Code=1-H1605-inline-bacterial-viral-cpap-filters&Store_Code=DHM&gclid=EAIaIQobChMIo-G35omi6AIVSrzACh29hwv3EAQYASABEgK9FPD_BwE

https://www.noinsurancemedicalsupplies.com/main-flow-bacterial-viral-filter/?sku=AV-7178&gclid=EAIaIQobChMIo-G35omi6AIVSrzACh29hwv3EAQYBiABEgKaUvD_BwE

Expensive and in demand but the real thing:
https://www.medtronic.com/covidien/en-us/products/mechanical-ventilation/filters.html

These info sheets on the above link's products may at least give some specs to work from 
https://www.medtronic.com/content/dam/covidien/library/us/en/product/ventilator-filters/dar-sales-sheet.pdf

Overall looks like most designs could be rigged up with a 3D printer or PVC fittings and an alternate filter material

jcl5m1, 2020-03-17:
added a link about inline filters to README  thanks!

richovercash, 2020-03-17:
Agree on the inline filter, and issues re impurities coming from a commercial motor. Also the NIOSH filter is VOC compliant which might be overkill, though it does offer an easily sourced mount.

HitoJima, 2020-03-18:
Needs to filter  VOCs, you dont want to allow any additional problems.  Everything post filter should be manufactured in ‘clean room’ conditions if possible.

richovercash, 2020-03-18:
I've got a concept for an inline filter here: 
https://1drv.ms/b/s!AjCTtwReRUpmiZMWODGYKpWxrK-bRA

Uses the 3M bayonet mount, 3M gasket, and 3M P95  filter. Its just a concept and I need some ME help making it work. Got a folder of 3D files ready to upload

richovercash, 2020-03-18:
[image]

Basic Concept

richovercash, 2020-03-18:
[image]
Uses existing P95 filter

clc, 2020-03-22:
Here's a configurable inline filter holder that I made:
https://www.thingiverse.com/thing:4233776 - should be able to take a wide variety of filters

jcl5m1, 2020-03-22:
that's really nice.  what are you thoughts about just making the tapered
press fit ends for the tubes. to get rid of the bayonet?
 also, do you think it would be possible to align the long axis of the
filter to be more parallel with the air flow (not making the tube come out
perpendicular from the filter).  That way more of the filter could be used
it might be more mechanically secure?

[image: image.png]

jcl5m1, 2020-03-22:
I guess the filter doesn't have to stay flat either.

clc, 2020-03-22:
How about:
[image]
for making the filter parallel with the air flow?

Same design file, just with tweaked parameters (increased hepa thickness, decreased hepa length/width).

For the "tapered press ends" are you talking about making the ends that connect to the tube more conical so they will slip into the tubes more easily or did you have a particular design in mind?

clc, 2020-03-24:
Updated https://www.thingiverse.com/thing:4233776 with a tapered end for the tube connector + made tube connector height a customizable property.

[image]

chakahamilton, 2020-03-24:
> You guys may want to take a look at some of these options:
> Cheap: [...]

I'm currently focusing my efforts on a PAPR   to use the Universal Inline Bacterial Viral Filter for CPAP Machines.

oiaohm, 2020-04-10:
The bad news here is that the intake filters as in the filter after the air source and before the mask should not be 3d printed.   These need to be molded  plastic.   3d printing like it or not makes a fairly rough surface that bacteria can in fact love being on.

Please note using silicon or injection or clay molding can all produce clean surfaces.

I am not sure how much airflow each Universal Inline Bacterial Viral Filter for CPAP is designed for.

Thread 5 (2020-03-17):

jcl5m1/ventilator #5: Efficient No Power Airway Shunt

axjjienn, 2020-03-17:
I think with respect to task (6) it is easy to have some-kind of spring loaded shunt, the problem would be making it power efficient. A potentially efficient way to do this would be a small servo which opens a hatch on the airway, that triggers when the power level reaches a certain "low" point. The issue with this is that it functionally decreases the power that can be run from any one-battery, as the "low" power point needs to be still above the complete discharge point of the battery, such that sufficient power remains to trigger and operate the airway shunt fail safe. It might be possible to create a pneumatic hatch, which opens when the flow rate drops below a certain rate, but these typically only work in continuous flow systems, which I am not sure we have here. Also, when starting the system, this hatch would need to be manually shut until steady state conditions are met.

jcl5m1, 2020-03-17:
interesting idea, I like the passive approach.  Perhaps some sort of mechanical latch where if the internal pressure drop down to ambient, the tube pops off.  only under high internal air pressure does it hold secure.  If i was a 3D printable element that would be great.

TheAmazingJarvis, 2020-03-17:
How about a simple flappy door? Airflow pushes the flappy element out of the way. No airflow and the flappy falls down.

[image]

omid-s, 2020-03-17:
> How about a simple flappy door? Airflow pushes the flappy element out of the way. No airflow and the flappy falls down. No electronics.
> 
> [image]

I was thinking of a same model but I was not sure if back pressure from breathing out could mess this up?

TheAmazingJarvis, 2020-03-17:
> I was thinking of a same model but I was not sure if back pressure from breathing out could mess this up?

I was wondering the same thing. One way to find out is to print one and try it.  Wish me luck.

TheAmazingJarvis, 2020-03-18:
> these typically only work in continuous flow systems, which I am not sure we have here

Therein lies a big question. When converting a CPAP into a respirator, would it stay on the whole time as they do now? 

(For people reading this who don't know the C in CPAP stands for Constant.)

TheAmazingJarvis, 2020-03-18:
I hooked it up to my CPAP machine and it works pretty darned well.

nbenci, 2020-03-18:
Use Tesla valve

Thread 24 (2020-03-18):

jcl5m1/ventilator #24: Collaboration

douglaswburke, 2020-03-18:
Hi Johnny.  My name is Doug Burke and I run a healthcare IT company called Cognitive Medical Systems (www.cognitivemedicine.com).  Two things:

1) We might be able to help with the arduino request and software needed to run the ventilator at different setting and for different patients and/or diseases.  My co-founder is a neonatologist and our CMIO is an anesthesiologist.  We work a lot with the DoD and VA and so some work in this area around automation and decision support in anesthesia and ventilation.

2) The DoD is about to release a "challenge" grant/competition where, from what I understand, the challenge will be to create a ventilator from common off the shelf parts for less than $200.  You should enter.  Send me an e-mail and I can let you know when the competition is live.

My e-mail address is:  dburke@cognitivemedicine.com

Thanks for doing this work!  Lots of interesting challenges at a critical time in healthcare delivery for the world.

Cheers - Doug

NoahGWood, 2020-03-19:
Hello Johnny and Doug.

I run a small quantum computing startup Spooky Manufacturing, we can assist in the circuit design and PCB prototyping of this device.

hobodrifterdavid, 2020-03-19:
Hello. Please also check Slack here: https://join.slack.com/t/open-ventilator/shared_invite/zt-cq0c2o4x-gXJLb0sZ4dVTUPt3oZy61Q

jcrubino, 2020-03-20:
Hi @douglaswburke and Johnny
I am a former LEVEL III NICU Registered Respiratory Therapist with ECMO transport experience and now professional software engineer working in python.  Let me know if there is a potential good fit for collaboration on this or future collaborations.

jcl5m1, 2020-03-24:
I could use help understand the existing options for ventilator tubing for managing inspirary/expiratory flow.  In particular how expiratory flow is prevented from going down the inspiratory circuit?, and how come inspiratory IPEP/EPAP doesn't create flow out the expiratory circuit?

DaveM135, 2020-03-24:
Hi Johnny

I believe these are valve controls that maintain flow directionality and line pressure (inspiratory pressure and end expiratory pressure).   The valves are generally either time or flow rate controlled depending on the mode of ventilation..  I’m referring to traditional mechanical ventilators or BiPAP machines in the case of noninvasive ventilation.   Perhaps there is a respiratory therapist on the thread who can provide the specifics or point us to the right technical references?

Best
Dave

nasocializes, 2020-03-25:
@jcrubino  Can you point to existing parts that are used in ventilator circuits that are readily available?

jcrubino, 2020-03-25:
For NIV there is an Exhaust valve (expired gas in the image) in the circuit.  Because of the back-pressure of the inspiratory line much of the exhaled air exits the exhale port.  Additional valves "peak plateau valves" are available to add for safety and better CO2 removal.

As mentioned in other issues, CO2 retention is a serious issue in NIV because the CO2 can often get pushed back into the circuit and re breathing of CO2 occurs.  

**Minute volumes in NIV are not guaranteed because of leaks around the mask and tube so monitoring of CO2 and satO2 are essential to gauge effective ventilation and oxygenation**

[image]

Because the lungs are more compliant than the exhaust valve in the circuit the positive pressure moves air into the lung first.  Vents often check or make available a vent circuit compliance test for aid in more accurate minute and tidal volumes.

jcrubino, 2020-03-27:
@nasocializes @jcl5m1 

[Mechanical Ventilator Milano (MVM):A Novel Mechanical Ventilator Designed for Mass Scale Production inResponse to the COVID-19 Pandemics](https://arxiv.org/pdf/2003.10405.pdf)

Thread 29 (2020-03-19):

jcl5m1/ventilator #29: Contact request: Dr. Sidney Merritt UCSD - endotracheal tube

jamescnelson, 2020-03-19:
Don't use this site often, looked hard for any other means to contact other than issue requests but a Dr. Merritt at UCSD is looking to speak with the Creator of this device as it's being discussed in med communities across the net regarding the addition of an endotracheal tube

619-543-6240
Email: skmerritt@ucsd.edu

jamescnelson, 2020-03-19:
[image]

AgentSmithers, 2020-03-21:
I'm a software engineer and have experience coding micro controllers to handle this logic. I would like to add my efforts to support this idea. Please let me know if there is anything I can do to help!

jamescnelson, 2020-03-24:
Contact Sidney Merritt at UCSD her email is in the support request. you may
want to work with her directly.

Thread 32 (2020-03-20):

jcl5m1/ventilator #32: Build a PAPR!

jcl5m1, 2020-03-20:
As I've learned more about the risk of high pressure care, it's definitely not for the faint of heart and can continue as an engineering thread.

I wanted share a much lower risk, less controversial application of the same parts - which is a Powered Air Purifying Respirator (PAPR).

https://github.com/jcl5m1/ventilator/wiki/Build-a-Low-Cost-PAPR

cbonitz, 2020-03-20:
Just a quick thought: Changing the configuration to push air through the filter, and having only the hose and the mask after the filter would turn any leakage from a safety issue into an efficiency problem. In the design you propose, leakage in the fitting between the filter and the pump or in the pump itself might cause the system to pull in contaminated air.

```
<-----------------+------------------------>
Negative Pressure |   Positive Pressure

    +------+   +----+                 +----+
    |Filter+---+Pump+-----------------+Mask|
    +------+   +----+                 +----+

               +----+   +------+ Hose +----+
               |Pump+---+Filter+------+Mask|
               +----+   +------+      +----+

```

jcl5m1, 2020-03-20:
ah, good point.

jcrubino, 2020-03-21:
HEPA h11+ filters might be a responsible alternative for this project to N95 filters needed in the healthcare center response.

Vacuum cleaners have been using them for years and making them widely available.

The foreseeable problem is deformation under pressure loads.

nasocializes, 2020-03-25:
@jcrubino  These are great ideas if you can prototype & test them.

jcrubino, 2020-03-25:
@nasocializes parts are on their way.

chakahamilton, 2020-03-25:
Here are the parts ive ordered from AMAZON for my PAPR Design. unfortunately, Their decision to only ship essential stuff means I have to wait until mid April to get everything. @jcrubino I too looked into using a UV light Source, but in my research found that it would have to be so intense it would require a lot of power. I could be wrong though in my interpretation. I plan to use HEPA Filters but am also trying to figure out how to "Sterilize" the incoming air which is almost impossible using a small footprint. I was also planning to power this system with Standard Drill batteries but will most likely settle on SLA Batteries 12V 10am for my motor size.

[image]

jcrubino, 2020-03-25:
@chakahamilton I understand the problem with UV light.  It needs to be a non ozone emitting UV light (which is usually the case if I understand, but 20 seconds of exposure is also needed.  I did not do any numbers on the strength of the light but I understand that has to be part of the equation.

The power source is another issue.  Light enough to be on a belt and rechargeable is ideal.  I like the cordless drill battery idea a lot.  We will need 3d printable designs for this.  

The cpap/vent filters are a great idea that I am using as well... but those might be hard to come by someday soon.

I am trying to come up with an inexpensive hood system for clinicians that is not scary for children.  T
T
he full face snorkel mask is indeed practical but for anyone wearing glasses and meeting with patients outside the wards it might not be conducive to clinic orientated tasks with people who may or may not be infected.  

Anyone know what the paper like material is... more solid then a walmart reuseable bag.  You can see the fibers, cheap and air tight?  Then how to fix a plastic material view portal to it with something better than hot glue?

Great ideas... lets keep the momentum up on this.

chakahamilton, 2020-03-26:
> @chakahamilton I understand the problem with UV light. It needs to be a non ozone emitting UV light (which is usually the case if I understand, but 20 seconds of exposure is also needed. I did not [...]

[These](https://www.amazon.com/dp/B07K6BK639) claim to be 395nm-405nm which in theory should work, but because UV light is not my wheel house I am unsure if that is the rating for the whole spool or each individual led.

I made these parts choices to  insure that it would be accessible for everyone to build. The idea of 3D printed parts is nice and all, but not everyone has access to those (I have 2). I also didn't want some one to need a full machines shop as well. So far I've used the following tools.

Drill
Step Drill Bit
Gorilla Tape
Hot Glue Gun
Xacto Knife

jcrubino, 2020-03-26:
I got an idea for respirator hoods.

I saw this today [DuPont expediting production of Tyvek hazmat suits for health care workers](https://www.nbcnews.com/health/health-care/dupont-expediting-production-tyvek-hazmat-suits-health-care-workers-n1169031) which is what I was looking for I believe.  

It can also be found (this and similar materials) in home stores as vapor barrier for new buildings. 

Any origami or seamstress/tailors out there for pattern making?

chakahamilton, 2020-03-27:
i'm using Rain jacket and pant for the suit, as tyvek and other professional jumpsuits are hard to come by or prices are extremely high and in addition to shipping/availability time.

chakahamilton, 2020-04-09:
I just finished building my first prototype of a PAPR based on my post [Above](https://github.com/jcl5m1/ventilator/issues/32#issuecomment-604093852)

[Video 1 Blower](https://photos.app.goo.gl/152azF1NSzZyT4S46)

[Video 2 The Face Mask](https://photos.app.goo.gl/EKKPcUzDHmcFNrf5A)

IT still need a little work but result so far are promising. I can breathe with the unit no problem. 
I plan to add Oxygen & Carbon Dioxide Sensors in the mask at some point.

oiaohm, 2020-04-10:
> @chakahamilton I understand the problem with UV light. It needs to be a non ozone emitting UV light (which is usually the case if I understand, but 20 seconds of exposure is also needed.

The bad news here all UV light that microbes and viruses makes ozone.  Dealing with produced ozone is a not simple.

https://en.wikipedia.org/wiki/Ultraviolet_germicidal_irradiation

Yes different frequencies of UV produce less ozone so make it simpler to remain under safe limits it also effects how much of it the air has to be exposed to.

"2011 Handbook, HVAC Applications, covers "Ultraviolet air and surface treatment" in Chapter 60"

This is noted in the wikipedia but you really do need get your hands on this and understand it before messing around with UV treatment of air.   Time of exposure alters based on flow rate and UV intensity and frequency.   20 seconds is only a really rough ball park.  Yes it comes a balancing act between ozone create and treatment speed.

jcrubino, 2020-04-10:
Modern germicidal lights should/are filtering out the light wave band that
creates ozone...

You need aprox 50 to 200 watts per square meter per second to disinfect
using a flourecent based UV light.

oiaohm, 2020-04-11:
> Modern germicidal lights should/are filtering out the light wave band that creates ozone... You need aprox 50 to 200 watts per square meter per second to disinfect using a flourecent based UV light.

This is horrible wrong on what is filtered out this will lead you into very big danger.

https://www.oxidationtech.com/ozone/ozone-production/uv-lamp.html
 The only section of the UV spectruim that does not produce ozone at all is UV-A band.     
UV-A does not work as germicidal .    Germicidal lights are UV-C that is 200 to 280 nm .   Yes link above 100nm-240nm ozone is made one way and 240-315nm ozone is made another there is not a single bit of the UV-C spectrum that does not produce ozone.  Yes 240nm makes ozone both ways.  So every bit of the germicidal lights frequency will produce ozone there is no way around this as it the nature of ozone production.  

Lets get to what they are in fact filtering out.

Now there are a few frequencies you avoid because UV way more effective at making ozone at those points.  Like you are going to want to filter out 254 nm out of UV-C Germicidal light because you get massive peak in ozone production at that point with that freq at 50-200 watts you are not going to stay inside safe values for ozone.

Basically the UV filtering on germicidal lights lowers the ozone produced does totally not stop ozone being produced.   This is the dangerous part you take a light design for a square meter of air and use it to process 1l of air instead you might end up with ozone above safe percentages.

Do also note Germicidal lights don't come with the one set of standard filters on them either the amount of watts a surface needs to be treated is linked to allowed frequencies of the germicidal lights also how many watts a area being treated can be treated with before you exceed safe ozone levels.  Welcome to nice fun.

Basically Germicidal Lights are very tricky items to play with and very simple things to totally screw up with.   Yes in a breathing system you would want a ozone alarm sensor.

There is also the confined space problem where the ozone in a room where you are using germicidal light can slowly increase over time.   Basically germicidal lights are not 100 percent safe and require serous due care.

richovercash, 2020-04-11:
Chaka,
Progress looks great!
I had similar idea using iRobot filter, Ryobi Battery, and motor/blower.
This is just a basic proportional model without any design.

Thanks + Best,
Rich Overcash
Industrial Design

This e-mail, including attachments, may include confidential and/or
proprietary information, and may be used only by the person or entity to
which it is addressed. If the reader of this e-mail is not the intended
recipient or his or her authorized agent, the reader is hereby notified
that any dissemination, distribution or copying of this e-mail is
prohibited. If you have received this e-mail in error, please notify the
sender by replying to this message and delete this e-mail immediately.

richovercash, 2020-04-11:
[image]

Chaka,
Progress looks great!
I had similar idea using iRobot filter, Ryobi Battery, and motor/blower.
This is just a basic proportional model without any design. Can place waisteband clip on backside. 

Looking for feedback. Attaching images here.

jcrubino, 2020-04-11:
@oiaohm 

I respect your critical take on UV light in general.  In addition to potential ozone production, there is the problem that most materials are not tested for UV-C band light.  

My comment was made in haste, perhaps too *lightly*.... a mention of some prior reading I have done on this.

Yes Ozone production is produced in much of the UV Band, yet using the reference you posted above... the facts you are sharing seem misinterpreted or I am not catching on to your rhetoric.

> Like you are going to want to filter out 254 nm out of UV-C Germicidal light ... 
[image]

The link you posted says 254 nm destroys ozone, and I have read this in other places as well.  I believe the grey area here is that most lights available cannot produce 100% within the specified narrow range, rather the stated wavelength on a UV light is the peak measurement.

oiaohm, 2020-04-11:
> @oiaohm

> The link you posted says 254 nm destroys ozone, and I have read this in other places as well. I believe the grey area here is that most lights available cannot produce 100% within the specified [...]
This diagram is not really fully covering the problem.  Peak of ozone destruction is still creating free Oxygen.   Yes that free Oxygen can link up and make O2 but it still can link up and remake O3 from the 254 nm side as well.  

Yes the grey area is a problem but even a correct UV freq light for ozone destruction will not produce air 100 percent ozone free all the time because of the destruction followed by recreating cycle that is not in basic diagram.

Yes grey area of UV light ratings mean you have some of the low frequency that will 100 percent produce ozone.

Please remember that free Oxygen does not have to just bind with O2 to make O3 or another free Oxygen to O2 like it could react with seals and other things.

> My initial concern, was that this approach is not practical considering that, circulated air has to be exposed to the uv light for a second at such wattage levels. For surfaces cleaning, this seems possible but... not for portable maker made ventilation device.

https://breathequality.com/germguardian-ac4825e-review/

I would not say it impossible devices like this are getting away with a 5watt light but the lot of considerations to get the chamber size to light to airflow rate right the wattage may not be that high.   Please note a device like these air purifiers  is not putting the air straight into a pipe/past seals that may not like free Oxygen.  They are also not aiming for 100 percent ozone free just not more ozone that what went in.

My brain was remembering it was not a free lunch.  I was thinking Ozone but the biggest problem here is free Oxygen reacting with materials its does not matter where in the Ozone altering section of UV you have this problem.  

I was remembering correct that Ozone does not magical cease to be something you can fail to monitor just because you use UV-C.   The free Oxygen problem was what I was getting mixed up on.   Notice both UV levels are going to make this problem remember free Oxygen really loves reacting with things and if it the  wrong things can the result can be start producing lots of heat leading to fire inside device.   Yes fire inside a breathing device would be really bad.

I am not saying don't play with UV but be really careful this can backfire badly.  UV-A is the only area you are not playing free Oxygen problem and that does not work for germicidal.

Sorry my brain was being stupid when I was reading those diagrams some how I was reading seeing O1 as O3.  Yes high volume O1 going into humans lungs does not do those the world of good either.   Basically you don't want O1 or O3 in large volumes going into human lungs.

chakahamilton, 2020-04-11:
> [image]
> 
> Chaka,
> Progress looks great!
> I had similar idea using iRobot HEPA filter, Ryobi 18V Battery, and motor/blower.
> This is just a basic proportional model without any design. Can place waisteband clip on backside.
> 
> Looking for feedback. Attaching images here.

@richovercash I really like that design. i hacked a filter holder together with Mock-up with a Radio shack project box hot-glue and gorilla tape. can you make it so the hole at the top accepts a standar CPAP hose (thats what I am using)

jarvik1984, 2020-04-15:
> I just finished building my first prototype of a PAPR based on my post [Above](https://github.com/jcl5m1/ventilator/issues/32#issuecomment-604093852)
>
> [Video 1 [...]

Wonderful job... I’m a physician and new to github but something similar to your prototype going. I’m trying to find a way to get portable power to the blower. My blower is DC 12V/8A m. I’ve also tried with a brushless radial blower that provides 42 CFM with a shorter tubing and a HEPA in-line filter but was not as good as it was with the electric air blower.
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

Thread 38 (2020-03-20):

jcl5m1/ventilator #38: Alarms: low airflow

amanzimdwini, 2020-03-20:
Not sure how easy - but you'd need an alarm when the airflow decreases (such as when the mask comes off the patient). Please add to your "to do list".
And yes, (1) last effort, and (2) probably best for PROVIDERS, not patients. GREAT idea, though - I am ripping an old CPAP apart right now

Istria1704, 2020-03-22:
The most robust and simple way I could think of:
Span a thin copper wire across the air channel and put a small (but constant) current through it.
The wire will heat up until it reaches equilibrium temp.

When air flows, the wire cools down. When air stops flowing, the wire heats back up.

Since resistance (Ohm) of the wire goes up with temperature rise, you could measure this "cycle" of increasing and decreasing resistance in the wire. If the cycle stops, you know something is wrong.

jcl5m1, 2020-03-22:
added to do's.

i ordered some nichrome wire, which gives 26 ohms/ft.  But, i actually
don't think
https://www.amazon.com/gp/product/B07CHTXZYW/ref=ppx_yo_dt_b_asin_title_o01_s00?ie=UTF8&psc=1

This reference has consideration of the material for hot wire anemometer.
But, seems have mixed material recommendations.
https://www.sciencedirect.com/topics/engineering/hot-wire-anemometer

I think this can be done with a low cost 24-bit ADC like the HX711
https://www.sparkfun.com/products/13879

I am also curious about ultrasonic flow sensors:
https://www.youtube.com/watch?v=Mkjw-iX6Af4

 I wonder if one of these can be re-purposed to do that.  It claim to have
0.3cm resolution.
rough velocity estimation in the tube is 50cm/s is 1.5% speed of sound.  If
I am doing the math correctly, does that mean to it has to be a 30cm long
tube that varies by 1% due creating a 1% deviation of 0.3cm that it can
detect it?
https://www.amazon.com/gp/product/B01COSN7O6/ref=ppx_yo_dt_b_search_asin_title?ie=UTF8&psc=1

jcl5m1, 2020-03-22:
I also curious about these air flow sensors used by engines:
https://www.autozone.com/engine-management/mass-air-flow-sensor

jcl5m1, 2020-03-22:
Looks like they even have 8 wire MAF sensors, that include flow, humidty, temp, and baro

https://www.youtube.com/watch?v=mFhovSdOY3g

I picked up a Bluestreak MF21029N 5-wire MAF sensor.  Still trying to figure out how to talk to it.

jcl5m1, 2020-03-23:
Got a link to an actual ventilator flow sensor:
https://www.sensirion.com/en/flow-sensors/mass-flow-meters-for-high-precise-measurement-of-gases/low-pressure-drop-mass-flow-meter/

jcl5m1, 2020-03-23:
https://www.sensirion.com/en/flow-sensors/sfm3xxx-sensor-platform/

jcl5m1, 2020-03-25:
worried about supply on these.  I can't buy anymore. I am curious if a differential pressure flow valve can be make with two MS5611s

jcl5m1, 2020-03-26:
I tried an automotive flow sensor.  It provides an analog flow signal.  

https://photos.app.goo.gl/UkC9ceGeRCVUVESo6

 For the part I used: MF21029.  This pinout is starting from flat side:
1. flow analog out (0-5v)
2. 5v reference from controller (unclear this is needed)
3. GND
4. 12v supply
5. temp analog out put (though this wasn't working for me)

jcrubino, 2020-03-27:
@jcl5m1 You want to make a "Manometer" for differential pressure measurements.
From this, along with the dimensions of the circuit you can use Poiseuille equations to determine the flow and volume.

MeatLasers, 2020-04-02:
The SFM3200 supply might indeed by tight for a while.
An alternative would Sensirion SDP800 sensor, which is used to measure the airflow in CPAPs. This should be available in very high quantities, and is also now available without any problems at Digikey.
More info:
https://www.sensirion.com/en/flow-sensors/differential-pressure-sensors/sdp800-proven-and-improved/
https://www.sensirion.com/fileadmin/user_upload/customers/sensirion/Dokumente/0_Corporate/Specialist_Articles/Sensirion_Specialist_Article_Gas_Flow_Bypass_EN.pdf

MikeJaworski, 2020-04-03:
I'm also interested in the issue of flow metering here - I'd already decided hot wire is the way to go as that's what commercial machines use but looks like the SFM3XXX series is out of stock globally and wouln't want to tax the medical supply chain anyway.

Can I ask how testing with automotive MAFs is going?  Which model?  Are they sensitive enough considering they are intended for use at much higher flow rates?

PS:  I also found ultra-cheap (£5.50 = $7 each) **bidirectional** MAFS:

https://www.te.com/commerce/DocumentDelivery/DDEController?Action=srchrtrv&DocNm=LMM-H03&DocType=Data+Sheet&DocLang=English&DocFormat=pdf&PartCntxt=G-MAFCO-005

This way you could easily measure inspired and expired flow, and calculate leak rate by difference.

Only issue is the linear portion of the sensor response is over the velocity range 20-40m/s

For standard 22mm ID breathing tubes, the velocity at 100LPM is only 4.3m/s so you'd be on a highly non-linear part of the response curve...

MikeJaworski, 2020-04-03:
OK, even better I found this DP flow evaluation kit from sensiron with flow element.

The bare DP sensors are about $12, evaluation kit with flow element is about $70.  You could 3D print flow elements, probably.  Evaluation kit flow element fits to medical tubing.

https://www.sensirion.com/fileadmin/user_upload/customers/sensirion/Dokumente/8_Differential_Pressure/Application_Notes/Sensirion_Differential_Pressure_Sensors_EK-P4_Flow_Element.pdf

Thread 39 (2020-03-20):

jcl5m1/ventilator #39: Over pressurization

fireb0lt, 2020-03-20:
I don't think that 20cm h2o is very high, nor would cause any lung trauma. My personal NIV mask setup tops out at 25cm and isn't even fully inflating my lungs. Cough assist machines go into the 60s-70s of pressure, even if it is for brief periods.

All this to say, we likely will have problems getting high enough pressures, don't need to really worry about over pressurization. As a FYI, I'm from Washington State where Covid-19 is out of control. My pulmonologist is one of the top in the nation (Dr. Joshua Benditt) and we talked about too high of pressures on my ventilator. He wasn't concerned.

jcl5m1, 2020-03-20:
interesting, i get mixed info on this.  I agree 20cmh2o doesn't feel high, but 45cmh2o kind of hurts as a healthy individual. I don't know how sensitive COVID patients can get.    I'd be interested in Joshua's read on the following:

https://github.com/jcl5m1/ventilator/wiki/Notes-from-chatting-with-a-pulmonologist

nasocializes, 2020-03-25:
Johnny: it seems like going above 20cm requires additional sensors to ensure safety. we'll continue to use 20cm as a cut off guidance until we have more capabilities.

Thank you! Closing for now to clean up the list.

closed 2020-03-25 by nasocializes

bradtem, 2020-03-25:
Consulting with some doctors who do ventilation, pressures are high in ARDS.   The alveoli are closed up and flooding.  Lungs are not compliant.   As such, ARDS ventilation is done with a very high base pressure (known as PEEP.)  Doctors are setting this to 16cm in may cases.  This is the lowest pressure, for exhalation.  The peak pressure varies, enough to deliver the required volume of air (or rather oxygen.)  Because the alveoli are so stressed, it is desired to deliver a very low volume of air, which means having a very high concentration of oxygen.   I have heard reports patients start at 95%, which can't be sustained because it is toxic but they get them going this way.   If the patient starts at 16cm, I suspect a peak pressure of 20cm will not help many patients.  Of course there are patients not needing the 16cm, or the higher peaks.    Also, you end up pumping nearly pure oxygen, which clearly is a risky thing to do near heat sources.  Just about anything can burn in that.

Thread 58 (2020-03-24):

jcl5m1/ventilator #58: Love to connect and collaborate from Cleveland

jephos, 2020-03-24:
Hello Johnny,

This is amazing work you've done on this thus far, and I woke up this weekend from my own CPAP wondering the same questions and started making calls.

I've also been in touch with Matt Hearn who has written a great medium article himself on the topic and has referenced your work, but yours has been the most comprehensive effort compiling facts and feedback that corroborates with many of my conversations today about the core issues around adapting CPAP's purposefully.

I'm working on getting a hold of Robert Chatman, whose book on fundamentals of ventilation mechanics you linked, who is from Cleveland.  I also have medical industry design firm interested and reaching out to their respiratory industry contacts.  BioEnterprise in Cleveland has also expressed interest and support, and there may be a proposal to Vulcan (US Govt) due this Wednesday that might be worth entering.

What is the best way to be in touch?

All the best,
JT Tan
JT at Case dot edu

nasocializes, 2020-03-24:
Per Johnny on another response:
Feel free to choose a to do, and reply to an existing issue, or create a
relevant one.

It will be easier to track work on github than via email.

DaveM135, 2020-03-24:
Hi both - am a pulmonologist/ICU specialist in SF Bay area.   Happy to set up some time to talk through what you've done.   I'm new to Github so may be missing better ways to collaborate. LMK how to be most helpful.   I have a background in biotech, medical devices, and clinical care.   Currently work in VC.

nasocializes, 2020-03-24:
Hi Dave. Thank you so much for the ping! Perhaps you can share your linkedin page so we can contact you through there without you having to leak your email :-) Johnny had a great chat with Michael McPeck, a respiratory therapist on Sunday and is now awaiting new parts to arrive. I'll check on when he's ready to chat with another pulmonologist. Thank you so much for reaching out!

jephos, 2020-03-24:
Hi @jcl5m1 @DaveM135 and @nasocializes , love to connect as you suggested.  Perhaps we could arrange a joint zoom video conference?

We love the PPE route, which we believe is one key outcome, but we're also exploring what the minimum set of adaptations could get us outcomes around the original mission that could be used 2/3 of the course of disease to alleviate the "1 respirator, 3 patients" problem that Italy faced.

I've talked with a few groups here who are working on the enclosure / filtration problem, and I've been in touch with Mike Hearn (who wrote this compile: https://blog.plan99.net/cpap-for-covid-d47886bf978c) who has been working the digital front hacking his Dreamstation.

@jcl5m1 @nasocializes Nasocializes, love to get your recommendation on how best to combine forces.

nasocializes, 2020-03-30:
FWIW, kanbans have been created to help project manage: https://github.com/jcl5m1/ventilator/projects

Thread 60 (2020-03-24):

jcl5m1/ventilator #60: Taking a stab at the To-Do's

sbate, 2020-03-24:
I'm a programmer and a rookie on the hardware side, but I took a stab at some of the todo's from a product design perspective related to volume, pressure alarms, etc.  The product is different after that and certainly no longer portable... however, it may steer someone smarter than me in the right direction and the pieces that were added are definitely low cost and readily available.  I'd love to hear feedback!

[Low Cost Ventilator Design.docx](https://github.com/jcl5m1/ventilator/files/4373545/Low.Cost.Ventilator.Design.docx)

nasocializes, 2020-03-24:
Hi sbate,
Awesome!
Can we use google docs so we can collaborate in real time?
I converted your word doc here:
https://drive.google.com/file/d/1zwDcfDHgT7lZHVNuVxvYmhZJPMkktJme/view?usp=sharing

You can request access after clicking on the link.

sbate, 2020-03-24:
Absolutely!  I requested access.

Also a question as to whether the need for an exhaust filter could be redirected.  An intake filter would still add value but at that point it wouldn't need to be N95.  If we have a pressurized system exhaust/exhaled air can be redirected to a container of alcohol, bleach, boiling water, or other deadly trap which would accomplish the same task without using scarce resources like an N95 filter.

jcl5m1, 2020-03-25:
@sbate - This looks great! Thanks for sharing the notes!

jcl5m1, 2020-03-25:
the biggest concern I have is around measuring the volume.  I haven't found an off the shelf way to do that easily. will comment in doc.

bradtem, 2020-03-25:
How accurately can volume be computed by knowing exactly how many revolutions the blower did, how many watts that took, and the measurement of pressure at one or more places?

ameeuw, 2020-03-25:
Hi everybody! Great project.

I think volume is usually integrated over the flow rate to the interface. The flow rate is measured using a differential pressure such as [this one](https://www.sensirion.com/en/flow-sensors/differential-pressure-sensors/sdp800-proven-and-improved/). Maybe cheaper alternatives from Aliexpress such as the MPX5010DP could work if they offer a similar pressure range.
Maybe calibration could get tough though..

sbate, 2020-03-25:
Sure thing - so there were two issues that made me shy away from measuring air.... first there were complications with patient pH if you weren't increasing the amount of oxygen in the air mix, and second measuring air is hard especially at variable pressures.  Measuring liquid is comparatively easy, so filling a an air reservoir (balloon) under water turns the air volume problem into a liquid volume problem which can be solved with a level gauge aka "how full is my bucket".  That full amount of air can be delivered consistently because we're not trying to calculate it on the fly while the patient's lungs are providing variable resistance.  Measuring before the inhale also opens this design up for many alternate forms of air compression, because the blower/compressor/inflater won't be fighting the patient lungs in real time, just a balloon under constant pressure.

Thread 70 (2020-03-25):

jcl5m1/ventilator #70: How quickly can the BLDC motor you pulled respond?

mikehearn, 2020-03-25:
From reading around it seems:

* Primarily it's bi-level machines that are interesting as quick ad-hoc ventilator replacements because they can generate much larger pressure differentials, making it easier to tolerate higher pressures.
* Bi-level machines *can* change their pressures by altering motor speeds, but often don't to reduce power and noise levels. Instead they throttle the air intake using a moveable vane/baffle.

Bi-level machines are rarer than CPAP machines. That raises the question of whether a CPAP machine can be quickly converted into a bi-level machine without the additional intake port throttle, by controlling motor speeds. As noise doesn't matter it seems mostly an electrical question. Have you studied the electronics inside the machine you disassembled to see what it would be theoretically capable of? The thinking here being that it's faster to reflash machines than make physical changes to them.

zobotek, 2020-03-26:
Interesting question.  I've started experimenting with mid-sized RC (e.g., quadcopter/airplane) motor controllers and motors in part due to their motor and controllers' closed-loop open-source programming (allowing PID tuning) and ability to deliver high controlled torque capable of rapidly and precisely delivering needed power changes, overcoming the significant angular momentum of props.  I don't know much about CPAP design, but it's not apparent to me why their motor speed controls would require rapid speed adjustments (in within 100ms).  Further, closed source motor control code may make appropriate PID tuning difficult.  

One paper with some data (and abundant dynamic analysis) may be found in International Journal of Mechanical Engineering and Robotics Research Vol. 4, No. 4, October 2015 "Design and Control of Small Quadcopter System with Motor Closed Loop Speed Control"
H. L. Chan and K. T. Woo.  It's available on line - Google for it.  It shows (in Tables I and II) precise and rapid changes in motor velocity that can be achieved with closed-loop control that can be tuned by access.

mikehearn, 2020-03-26:
I guess it's because breathing can turn around from inhalation to exhalation very quickly, so the time between user breathes out + sensor latency + controller latency + motor latency needs to be low enough that the user isn't breathing against the pressure (which is hard).

RWL-69, 2020-03-29:
Normal Breathing Pattern (Normal Respiration Cycle)
[https://www.normalbreathing.org/patterns-normal/](url)

Turn around time in a person is slow in comparison to a drone requirements.  If you look or think about breathing, it isn't instant.  Think in terms of the number of breaths in a minute.  Watching videos and taking a crash course on ventilators has shown me that most motors will work change fast enough.  Normal breathing rates range from 60 breaths per minute (infants) to 12 for adults.  I would look at rates changing in 10 to 50ms would be fast enough.

There is a YouTube video by Medcram that explains how ventilators work with nice drawings of the various breathing cycles under ventilator control.
[https://www.youtube.com/user/MEDCRAMvideos](url)

Motor requirements and control would depend on the mode being used.

In my work, it is usually the other way, looking for pico or nanoseconds, so breathing is in terms of seconds is very slow.

zobotek, 2020-03-29:
I completed a 3D-printed turbine and mounted a 35mm RC plane/quadcopter
motor in it this morning.  I can run tests that characterize its time
constants and pressure/volume delivery.  The speed controller that I am
coupling it with is rated for 20A and outputs a pulse for each motor
revolution for rotational speed measurement and monitoring.  Note that this
motor is compatible with a 2-2kg quadcopter.  The motor torque, closed-loop
controller design and lightweight  (13.3g) 67mm turbine are _much_ more
capable of rapid rotational velocity change than a common computer fan.

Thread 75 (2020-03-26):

jcl5m1/ventilator #75: HEPA FILTERS?

Fearfulbot, 2020-03-26:
According to OSHA 29CFR1910.134, Hepa Filters are considered an alternative when N95 & N100 masks have been depleted.

https://www.sears.com/hoover-genuine-hoover-t-series-exhaust-hepa-filter/p-SPM9466216917

These are normally used in vacuum applications, which is why they're still available

chakahamilton, 2020-03-26:
> According to OSHA 29CFR1910.134, Hepa Filters are considered an alternative when N95 & N100 masks have been depleted.
> 
> https://www.sears.com/hoover-genuine-hoover-t-series-exhaust-hepa-filter/p-SPM9466216917
> 
> These are normally used in vacuum applications, which is why they're still available
> 

> Has anyone tried this? Would they be viable for the PAPR system?
I will be testing them out in a design I am working on. it will use 2 of them  on apposing ends depending on the motors capabilities.

jcrubino, 2020-03-26:
you need h11+ to replicate a N95

H13 filters are fairly standard but there is a risk that the knock off and off brand market are not up to the technical standards of a true Hepa Filter rating at 11+

jcrubino, 2020-03-26:
[Hackaday Article on household filter materials](https://hackaday.com/2020/03/18/homemade-masks-in-a-time-of-shortage/)

Fearfulbot, 2020-03-26:
The term "HEPA vacuum'' is defined as a vacuum which has been designed with a HEPA filter as the last filtration stage. A HEPA filter is a filter that is capable of capturing particles of 0.3 microns with 99.97% efficiency. The vacuum cleaner must be designed so that all the air drawn into the machine is expelled through the filter with none of the air leaking past it."

Is the 99.97% efficiency equivalent to a H11

jcrubino, 2020-03-27:
> Is the 99.97% efficiency equivalent to a H11
  No.  An H11 is rated at 95%.  It was first brought up in the context of an easy to find N95 mask replacement.  We will need a H13 HEPA filter for that comes in at 99.95% total retention rate of 0.3 Micron particles.  This equation becomes a little more difficult if we are to consider the Corona Virus 19 is 0.1 microns in size.  "Better than nothing" and "close" is better than nothing and better than depleting medical supplies from professional healthcare workers and facilities.  Your philosophy may vary.

> The term "HEPA vacuum'' is defined as a vacuum which has been designed with a HEPA filter
   HEPA stands for High-efficiency particulate air AKA high-efficiency particulate absorbing  or high-efficiency particulate arrestance is not defined by the direction of the flow of air.  If this is too liberal a definition let me know.  

The motive for using a HEPA filter is to find easily available parts to create functional respirators and ventilators, not medical grade machines ready to go to market or be put to use in the healthcare setting.

We chose to make ventilators not because it is easy, but because it is difficult and builds a cultural cache of ingenuity using simply available parts.

zobotek, 2020-03-29:
Yes, I've been making bayonet-style 3M 6000/7000 series N100 filter cartridges from HEPA vacuum cleaner bags and 3D-printed ABS frames.  To ensure a sealed surface and low leakage of micro-particles, the frames can be acetone-sprayed or painted.  The filter media I've been using has 3 interior layers of non-woven synthetic fiber surrounded by a synthetic non-woven fiber shell.  It is hot-cut (~190C tool) to the needed shape, sealing the edges.  After cutting, the filter medium is glued to the frame.  The non-foaming polyurethane gule remains somewhat flexible when cured.  The filter medium can be peeled off and the frame reused.  Note that baking an object at 60C/140F for 1/2 hour or so is reported to titrate the SARS coronavirus by a factor of 100,000 or more.   [ https://link.springer.com/content/pdf/10.1007/s00430-004-0219-0.pdf ] .  While this would clearly not kill all bacteria & virus, IMHO it's more than enough to disinfect covid-19, allowing filter reuse without even replacing the filter medium where covid-19 filtration is the objective.  

The 3D-printed air turbines I've constructed and am evaluating for improvised ventilator use are designed to have inlet and outlets filtered by HEPA/P100/N100 filters that are compatible with 3M bayonet masks, whether improvised or factory-built.  

HEPA filter material is considerably more flow-resistant than standard vacuum cleaner filter material.  So much more surface area is needed for the same pressure and flow.  

And yes, there is fraud potential _almost_everywhere_, even in supposedly medical-grade equipment.  While they may not seal well and it's not difficult to understand why an N100 or P100 mask is safer.

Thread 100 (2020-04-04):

jcl5m1/ventilator #100: Oxygen Sensor, why not blood oxygen sensor (oximeter) instead?

leakydata, 2020-04-04:
Since your primary concern is the oxygenation of the patients blood, couldn't you use a solenoid valve on an oxygen tank, which would be controlled by a blood oxygen sensor like the max30100 or max30102. That way you wouldn't have to worry about the oxygen in the flow of air (the inspiration), but instead could just add oxygen, at a constant rate, to the stream until the patients' levels began increasing or hit a threshold set by a clinician. Then the system could continuously open and close the valve on the oxygen tank in response to the patients need; in a feedback loop between the patient and the oxygen tank.

MikeJaworski, 2020-04-04:
2 comments:

1) This is going to be quite laggy

2) All the medical device standards call for direct control of Fi02

jcrubino, 2020-04-05:
A pulse oximeter works by measuring the hemoglobin 02 saturation through light refraction tuned to hemoglobin.

Oxygen sensors for devices are measuring the gas concentration.

sanketkelkar12, 2020-04-06:
I would like to suggest that will it be effective if a feedback from blood oxygen level monitor is taken via Bluetooth and the same could be used to control the speed of blower?

MikeJaworski, 2020-04-07:
See point 1 above.

Response time is going to be >1minute.  Have fun tuning that PID loop.  PS you can't just adjust blower speed to force more air in, you'll rupture the patient's lungs.  You'd need to be much more advanced than that - increasing PIP until a limit is reached, then increasing cycling rate between PIP and PEEP after that.

jcrubino, 2020-04-07:
> Since your primary concern is the oxygenation of the patients blood...

The clinical standard is to get an arterial blood gas which measures paO2, paCO2 and HCO3.  If the patient has chemical poisonings the hemoglobin, specifically the pulse oximeter is not an accurate measure of oxygenation.

marcocamisanicalzolari, 2020-04-19:
There is annoxygen sensor controlled by an App. It could work using an Arduino module to read the value of the sensor

mmcpeck, 2020-04-29:
jcrubino is correct. Pulse oximeters estimate oxyhemoglobin saturation (SpO2) non-invasively. An arterial blood gas (ABG) is an invasive test that measures PaO2 (partial pressure of oxygen in arterial blood) plus other things. There is a relationship between arterial blood oxygen saturation, SaO2 (dependent variable), and PaO2 (independent variable); it is called the oxyhemoglobin dissociation curve. It is an S-shaped, non-linear curve (although the middle is relatively linear). In the upper region of the curve, large changes in PaO2 (which could be diagnostically important in a sick patient) result in only small changes in SaO2. For a patient breathing room air (21% FIO2) a pulse oximeter provides valuable information. But once a patient is on elevated FIO2, the PaO2 can easily be 150 to 300 mmHg or more and the SpO2 doesn't mean as much as changes in PaO2 relative to FIO2. 
     There have been attempts at making miniaturized PO2 electrodes that can be inserted intra-arterially to enable continuous real-time PaO2 readouts, but a reliable device has yet to be developed. All past designs have had difficulty with maintaining accurate measurements over time due to protein buildup over the poles of the micro-Clark electrode or micro-FET. As mentioned by others, real-time SpO2 monitoring is too slow to pick up clinically significant changes in PaO2. And real-time PaO2 monitoring just doesn't work for very long. Thus, closed-loop feedback control of O2 therapy and ventilatory devices has not become an everyday reality at this time. 
     Besides, a ventilator regulates ventilation, which controls CO2 excretion. If you wanted to control the ventilator via feedback from a physiological parameter, you would want to use the arterial carbon dioxide tension (PaCO2) as an indicator since PaCO2 is inversely related to minute ventilation (rate x tidal volume) and directly related to CO2 production. There are devices known as capnographs or capnometers that measure CO2 in respiratory gases and considerable research has been done and is underway with respect to closed-loop control of the ventilator based upon exhaled CO2. However, it turns out to not be quite so simple as there is a multitude of inputs that go into managing a ventilator patient, and doing so on the basis of a couple of physiologic transducer signals ignores many other important factors.
     I'm a respiratory therapist and pulmonary physiologist; most of you are engineers. To solve certain problems, we need each other.  
[image]

mmcpeck, 2020-04-29:
I just spent 20 minutes writing a nice little piece on SpO2, PaO2, the oxyhemoglobin dissociation curve, and closed-loop control of mechanical ventilators. Somehow it got lost in the ether. I'm too tired to do it again.  Anyway, at the end I said I'm a respiratory therapist and pulmonary physiologist and many of you are engineers. To solve many of these issues, we need each other.

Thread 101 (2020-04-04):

jcl5m1/ventilator #101: Moisture or a moisturizer is needed in any ventilator system.

leakydata, 2020-04-04:
Moisture is a necessity in any ventilation system, because it is important that the lung tissue is not dried out. This issue is usually handled by hardware in the system that adds moisture, or special inline filters or devices. Are there plans to manage moisture in the system?

MikeJaworski, 2020-04-05:
Could an off-the-shelf nebuliser be teed into the flow path?  They are cheap(ish) at about £50 and already designed / approved for the job.

For example:

https://www.philips.co.uk/c-p/HH1340_00/innospire-essence-compressor-nebulizer-system

jcrubino, 2020-04-06:
You do not want to have to rely on nebulization for humidification.
COVID and other respiratory pathogen illnesses require hospitals to limit the amount of aerosol produced and in contact with the patient.

A heater water device is most desirable especially for secretion clearance, HME (Heated Moisture Exchanger) is suitable for keeping the internal respiratory tract humidified.  HME are usually a filterpaper device in the breathing circuit close to the ET tube.

jcrubino, 2020-04-07:
@Col68 congratulations on your progress.
I believe you are telling us you are close to finishing a PAPR (Positive Air Pressure Respirator).

For the purposes of clairty,  using a "nebulizer" for humidity is not ideal for ventilator purposes.
A medical nebulizer will create excess vapor that is only useful for short periods of time (medication delivery).  Patients with ARDS and COVID do not need excess vapor entering their respiratory tract as it will consolidate into macro water droplets hindering their already "wet" lung from the immune response.  Additionally, it could create a contact vapor hazard in the room where healthcare workers are.  The healthcare workers will absolutly need a PAPR with respiratory droplet grade filtering in such a situation.

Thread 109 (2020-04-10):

jcl5m1/ventilator #109: PAPR current design issues.  And have you considered cyclonic separation as part of design

oiaohm, 2020-04-10:
1 random electrical tape very bad idea.   Depend on brand of electrical tape this stuff can be treated with different anti rodent chemicals including stuff like Warfarin (Coumadin) so if you want someone  to be using something and end up bleeding out out eyes use any random electrical tape in a breathing air system.   Also some brands of electrical tape have different Flame Retardant chemicals some not human friendly because they can be cancer agents with long term direct exposure.   Also there is a solvent problem from the glues they can use.  Finally some brands will give you a lead problem as well.

There is HVAC/R rated electrical tape there is also the HVAC/R rated clear and duct tapes as well that when in contact with air flow are safer than the HVAC/R electrical tape.   So even when you are using the right tapes you are not meant to use the electrical tape to seal up general air leaks that is what the clear HVAR/R tape or duct tape is for.   Yes for a prototype using the wrong tape I can understand but you should not keep on using the wrong tape long term.  Basically when it comes it air stuff that humans/animals will be breathing electrical tape is only for electrical stuff you have other tapes for the duct work to guide the air flow and it important to use them.

Also don't forget HVAC/R is not any old electrical tape or any old tape for the duct work.

2. you want molded parts if possible.   So parts need to be design with the concept they will be molded at some point.  The surface of 3d prints is not ideal for this usage its normally too rough and allowing of bacteria growth.   Yes in emergencies when you can disregard basic safety they will allow 3d printed parts. 

3.  Question what is the required airflow.  I guess general 120mm computer fan cannot provide it?

4.  Common issue with PAPR systems is when using them in less than clean air that there operational time between filter changes is reduced massively.  In theory there is a solution to this.

https://en.wikipedia.org/wiki/Cyclonic_separation

Do notice how many bagless vaccum cleaners are in fact using Cyclonic separation.   So if first stage filtration was Cyclonic this would reduce the material the rated filter material would have to trap.

Yes the idea of using hepa filters out of vuccum cleaners miss that you have a stage 1 filteration of either the bag or cyclonic separation before the hepa filter this is important to long time operation of that filter.

Yes people sourcing and converting filters design for other things for masks are normally losing the stage 1 filtration this results in that the material will be taking large material than it designed to.

Adding a stage 1 filtration to even to filters designed for masks will improve functional time because they will not come packed with material as fast.

Lets not just try to make a PAPR lets try to make a PAPR that has a feature that most of the common ones are missing. 

There are many materials that can get to  N95/p2 and above like thick towelling but these require some from of forced air system to make them functional.

3dseed, 2020-04-10:
@oiaohm GREAT comments..!!
So going with a forced air system and thick toweling could be a solution ?
Currently we can't even get filters here in Barcelona.. desperately looking for other options.
So we just need the right size air pump and thickness of towel ?
We have the mask files online here.. but need to source the components before we can make the [silicon mask](https://3d-seed.com/open-source-masks/)..

jcrubino, 2020-04-10:
@3dseed [Blue Shop Towels](https://www.businessinsider.com/homemade-mask-using-hydro-knit-shop-towel-filters-better-2020-4) are getting some traction for filter materials

oiaohm, 2020-04-11:
> @oiaohm GREAT comments..!!
> So going with a forced air system and thick toweling could be a solution ?
> Currently we can't even get filters here in Barcelona.. desperately looking for other options. [...]

https://www.researchgate.net/publication/258525804_Testing_the_Efficacy_of_Homemade_Masks_Would_They_Protect_in_an_Influenza_Pandemic

Yes it could be a solution to use fabric towelling of the right weave and density.  Like this study with the tea towel towelling using 2 layers got you to a n95.   Problem is the air resistance to breathing not the filtering.   Of course you may want to use more layers for longer operational duration before filter is breached that going to equal more resistance.

Please note you will need the testing gear as each weave of towelling has different filtering behaviour.

> @3dseed [Blue Shop Towels](https://www.businessinsider.com/homemade-mask-using-hydro-knit-shop-towel-filters-better-2020-4) are getting some traction for filter materials

Sorry to say jcrubino those shop towel are not anywhere near a close to n95 it does not take much to win against a surgical mask on face because they were not design to filter the air you breath in only out.   Material of a surgical mask if you can get it to fit well beat shop towel hands down also comes a hindrance to breathing.

Note the 2013 one went back to 50 percent of a n95 mask on filtering to prevent hindrance to breathing.

Your standard n95 mask materials are particular designed to be low hindrance to breathing while providing the filtering.

Now if we can remove the hindrance to breathing problem with a motor/blower the list of materials that can do N95/R95/P2 filtering and above increases massively.   Of course the resistance is going to cause to reduced battery time in operation.

If you are using towelling I would be recommending Cyclonic separation pre filter so large dust in air are not going into the towelling and wedging the fibers open.

I really don't see why cyclonic separation cannot be used air in take of blower and filter placed after blower.

Lot of ways I can see take your hepa cyclonic separator vaccum cleaner as a model.   Some of those with a washable fabric filter is still above a n95 heck above a r95/p2 in filtering.   When you look at your standard on market PAPR they are not designed this way.   There is no as much profit making a item that has washable filters.

Yes washable filters at n95/r95/p2 and above are not 100 percent safe for a person to use directly due to too much air resistance.   Now powered is a completely different item here as the electronic motor gets to over come the resistance problem.

Please note I don't say what I am suggesting is ideal.   But I am willing to trade battery life/operational time frame to in fact have a operational mask that is not trying to kill me it self and will filter out what is required.

I am after a operational mask not to protect me from covid-19 but to protect me from oil sprays that I have to spray on crops to protect them from pests.   The nightmare is I cannot get p3 or p2 masks here in Australia for that job.  So I am back to old school fabric towelling masks with their risks to life due to excessive air resistance.  Yes hospitals have taken most of the supplies that go to agriculture here. 

So a good design PAPR using fabric towelling would be safer than what I am currently using.

Yes being used in agriculture  the air will not always be dust free like a hospital.

chonghorizons, 2020-04-11:
This is helpful. And, I have a question. My main concern is cost and complexity. Do you know of an easy $20 or less cyclonic configuration? Preferably without 3d printing (I know I'm making wild/hard design demands).  Maybe with two PVC tubes, one inside the other?

The other thing to note is this came out 4 days ago and avoids the filter issue with what they say are readily available hospital viral filters: 

** MAIN HALO DESIGN **
https://www.youtube.com/watch?v=JMXP8jAmDKA&feature=youtu.be
and 
https://3dprint.nih.gov/discover/3dpx-013544

chonghorizons, 2020-04-11:
>>> Question what is the required airflow. I guess general 120mm computer fan cannot provide it?

A 120mm computer fan is probably okay. We have some links (on the Halo, Washington state youtube comments) that says that 20 L/min (1/2 cfm) may be sufficient, but that maximum respiratory load is more like 4-15cfm.  We also suggested a "trademill test" that monitors O2 as an acceptable way to test if a PAPR is sufficient.  

See CoronavirusNotAlone comment that includes this:

##### Youtube comment
f you want to focus on respiration rate, 4cfm is what we found.   Quoted:  4-15cfm is what is needed for human breathing (https://www.google.com/search?q=human+breathing+cfm)   Hard to get exact numbers.  This has a chart for breathing peak by age: https://biology.stackexchange.com/questions/5466/what-is-the-inlet-outlet-speed-of-air-going-in-out-of-our-mouth-during-inhalatio

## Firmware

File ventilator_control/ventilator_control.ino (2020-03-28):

// originally written by Johnny Lee <jcl5m1+ventilator@gmail.com>

#include <Servo.h>

Servo myservo;  

//some variables to tweek
#define version "20200316.2"
#define rate 16 // breathing cycles per minute
#define enable_motor true // useful for debugging without noise

#define max_speed 180
#define min_speed 0
#define PEEP_speed 40 //approx 5cm/H2O
#define led_pin 13
#define button_pin A5
#define current_pin A0
#define servo_pin 3
#define serial_baud 9600

int buttonState = 1;
int buttonStatePrev = 1;
int speed_state = 0;
int loop_count = 0;
int click_loop_count = 0;
int click_count = 0;

int target_speed_high = 0;
int target_speed_low = 0;

int cycle_counter = 0;
int cycle_phase = 0;
int mode = 0;
int current = 0;


void setup() {

  Serial.begin(serial_baud);
  Serial.print("Version:\t");
  Serial.println(version);

  pinMode(led_pin, OUTPUT);
  pinMode(current_pin, INPUT);
  analogReference(INTERNAL); // sets reference to 1.1v
  pinMode(button_pin, INPUT_PULLUP);
  digitalWrite(led_pin, HIGH);

  if(enable_motor){
    myservo.attach(servo_pin,1000,2000); // some motors need min/max setting
    
    Serial.print("Initializing ESC...");
    
    myservo.write(max_speed);
    delay(3000); // wait for esc to boot, and sample maximum
    myservo.write(min_speed);
    digitalWrite(led_pin, LOW);
    delay(2000);  // wait for esc to sample minimum

    digitalWrite(led_pin, HIGH);
    myservo.write(PEEP_speed);
    Serial.println("Done");  
  } else {
    Serial.println("Motor disabled.  Bypassing initialization");      
  }
}

void loop() {

  buttonStatePrev = buttonState;
  buttonState = digitalRead(button_pin);

  // button down event, accumulate number of clicks and time of first click
  if(buttonState == 0 and buttonStatePrev == 1){
    click_loop_count = loop_count;
    click_count += 1;
  }

  if(click_count > 0){
    // past click count timeout
    if(click_loop_count + 30 < loop_count){
      if(click_count == 1){ // single click
        speed_state = (speed_state + 1)%5;
        if(mode == 0){
          cycle_counter = 10000; // if in CPAP mode update immediately
        }
      }
      if(click_count == 2){ // double click
        mode = (mode +1)%2;
        // if entering PEEP mode, update immediately in exhale cycle
        // otherwise, maintain phase
        cycle_phase = 0;
        cycle_counter = 10000;
      }
      // blink LED
      digitalWrite(led_pin, LOW);
      delay(50);  
      digitalWrite(led_pin, HIGH);

      // print state
      Serial.print(loop_count/100.0);
      if(mode == 0){
        Serial.print("\tset to CPAP level: ");
        Serial.println(speed_state);
      }
      if(mode == 1){
        Serial.print("\tset to PEEP level: ");
        Serial.print(speed_state);
        Serial.print("\tforced rate: ");
        Serial.print(rate);
        Serial.println("/min");
      }
      click_count = 0;
    }
  }

  // approximate pressure mapping fro original blower. Other blowers will vary
  // 40 ~= 5cm/H2O
  // 60 ~= 10cm/H2O
  // 90 ~= 18cm/H2O
  // 120 ~= 32cm/H2O
  
  if (speed_state == 0) {
    target_speed_high = 60;
    target_speed_low = PEEP_speed;
  }
  if (speed_state == 1) {
    target_speed_high = 70;
    target_speed_low = PEEP_speed;
  }
  if (speed_state == 2) {
    target_speed_high =  80;
    target_speed_low =  PEEP_speed;
  }
  if (speed_state == 3) {
    target_speed_high =  90;
    target_speed_low =  PEEP_speed;
  }
  if (speed_state == 4) {
    target_speed_high =  100;
    target_speed_low =  PEEP_speed;
  }
  
  //CPAP mode, both speed are the same
  if(mode == 0)
    target_speed_low = target_speed_high;
    
  // handle breath in/out cycle at target rate/min
  cycle_counter += 1;
  if( (30*100)/rate < cycle_counter){
    cycle_phase = (cycle_phase+1)%2;
    cycle_counter = 0;
    Serial.print(loop_count/100.0);
    Serial.print("\tphase speed:");
    if(cycle_phase == 0){
     if(enable_motor)
        myservo.write(target_speed_high);
      Serial.println(target_speed_high);
    } else {
     if(enable_motor)
        myservo.write(target_speed_low);
      Serial.println(target_speed_low);
    }
  }

  // for debugging breathing back pressure sensing
//  current = analogRead(current_pin);
//  Serial.print(current);
//  Serial.print(",");
//  Serial.println(digitalRead(button_pin));
  
  loop_count += 1;
  delay(10);  // approximately 100 cycles per second
}

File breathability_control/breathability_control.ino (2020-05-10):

#include <Servo.h>
#include <Wire.h>
#include <MS5611.h>
#include "sensirion3200.h"

#include <LiquidCrystal_I2C.h>
LiquidCrystal_I2C lcd(0x27,20,4);  // set the LCD address to 0x27 for a 16 chars and 2 line display

char msg[20];
char str_tmp[20];

#define BUTTON_PIN 4
#define BLOWER_PIN 5

int target_speed = 0;
int target_flow = 0;
int state = 0;
int prev_button = 1;
int flow = 0;
int flow_smooth = 0;
int flow_smooth_prev = 0;
int delta_smooth = 0;
Servo myservo;  
#define max_speed 18000
#define min_speed 0
#define led_pin 13
#define FLOW_CONVERSION 115

MS5611 pressure_sensor(&Wire);
float pressure_sensor_zero = 0;
float pressure_smooth = 0;
#define PRESSURE_ZERO_SAMPLES 100
#define mbar_to_cmh2o 1.01972

// get local ambient pressure
void zero_sensor(){
  pressure_sensor_zero = 0;
  delay(50);
  pressure_sensor.ReadProm();
  for(int i = 0; i < PRESSURE_ZERO_SAMPLES;i++){
    pressure_sensor.Readout();
    pressure_sensor_zero += pressure_sensor.GetPres();
  }
  pressure_sensor_zero /= (PRESSURE_ZERO_SAMPLES);    
}

// flow table - open air, aprox conversion  115
// 0 - 0 l/m
// 3771 - 34 l/m  * extrapolated
// 7100 - 64 l/m
// 10600 - 90 l/m
// 13800 - 116 l/m
// 16800 - 141 l/m
// 19600 - 165 l/m

void setup() {
  // put your setup code here, to run once:
  Serial.begin(9600);
  Serial.println("Blower Control v0.2");
  
  sprintf(msg, "Init LCD:");
  Serial.print(msg);
  
  
  lcd.init();  //initialize the lcd

//  Wire.begin();
  //disable internal pullups to support 3.3v I2C
  pinMode(A4, INPUT);
  pinMode(A5, INPUT); 
  lcd.backlight();
  lcd.clear();

  Serial.println("OK");
  
  pinMode(BUTTON_PIN, INPUT_PULLUP);



  lcd.setCursor ( 0, 0 );
  sprintf(msg, "Init flow sensor:");
  lcd.print(msg);
  Serial.print(msg);
  init_flow_sensor();
  sprintf(msg, "OK");
  lcd.print(msg);
  Serial.println(msg);


  lcd.setCursor ( 0, 1 );
  sprintf(msg, "Init press sensor:");
  lcd.print(msg);
  Serial.print(msg);
  pressure_sensor.setI2Caddr(0x77);
  while(pressure_sensor.connect()>0) {
    sprintf(msg, "ERR");
    lcd.print(msg);
    Serial.println(msg);
    delay(500);
  }
  
  zero_sensor();
  sprintf(msg, "OK");
  lcd.print(msg);
  Serial.println(msg);    

  myservo.attach(BLOWER_PIN,1000,2000); // some motors need min/max setting
  lcd.setCursor ( 0, 2);
  sprintf(msg, "Init blower:");
  lcd.print(msg);
  Serial.print(msg);
  
  myservo.write(max_speed);
  delay(3000); // wait for esc to boot, and sample maximum
  myservo.write(min_speed);
  digitalWrite(led_pin, LOW);
  delay(2000);  // wait for esc to sample minimum

  digitalWrite(led_pin, HIGH);
  myservo.write(min_speed);
  sprintf(msg, "OK");
  lcd.print(msg);
  Serial.println(msg);
  
  delay(1000);
  lcd.clear();

}

void loop() {
 
  flow = read_flow();
  flow_smooth = 0.9*flow_smooth + 0.1*flow;

  pressure_sensor.Readout();
  float relative_pressure = mbar_to_cmh2o*(pressure_sensor.GetPres()-pressure_sensor_zero);
  pressure_smooth = 0.9*pressure_smooth + 0.1*relative_pressure;
  // put your main code here, to run repeatedly:
  int button = digitalRead(BUTTON_PIN);
    
  if(!button && prev_button){
    state += 1;
    if(state == 3){
      state = 0;
    }    
  }
  prev_button = button;

  if(state==0){
    target_flow = 0;
    target_speed = 0;
  }
  else if(state == 1)
    target_flow = 34*FLOW_CONVERSION;  // 34 L/m
  else if(state == 2)
    target_flow = 90*FLOW_CONVERSION; //90 L/m

  int p = target_flow - flow_smooth;
  int d = flow_smooth - flow_smooth_prev;
  delta_smooth = 0.9*delta_smooth + 0.1*d;
  target_speed += p/10-d;

  flow_smooth_prev = flow_smooth;
 
  if(target_speed > max_speed)
    target_speed = max_speed;
  if(target_speed < min_speed)
    target_speed = min_speed;
  myservo.write(target_speed/100);

  lcd.setCursor ( 0, 0 );
  sprintf(msg, "Target Flow: %3d L/m", target_flow/FLOW_CONVERSION);  
  lcd.print(msg);
  lcd.setCursor ( 0, 1 );
  sprintf(msg, "Meas.  Flow: %3d L/m", flow_smooth/FLOW_CONVERSION);  
  lcd.print(msg);
  lcd.setCursor ( 0, 2 );
  dtostrf(pressure_smooth/100, 4, 1, str_tmp);
  sprintf(msg, "Press: %s cmH2O ", str_tmp);
//  sprintf(msg, "Blower Speed: %3d%%", target_speed*100/max_speed);
  lcd.print(msg);
  lcd.setCursor ( 0, 3 );
  if(target_speed == max_speed) {
    sprintf(msg, "Status: Max Speed  ");      
  }else {
    if((abs(p) > 2*FLOW_CONVERSION) || abs(delta_smooth) > 10)
      sprintf(msg, "Status: Adjusting ");  
    else
      sprintf(msg, "Status: Ready     ");  
  }
  lcd.print(msg);

 
  Serial.print(target_flow);
  Serial.print(',');
  Serial.print(flow_smooth);
  Serial.print(',');
  Serial.print(relative_pressure/100);
  Serial.print(',');
  Serial.println(target_speed*100/max_speed);
  delay(0);
}

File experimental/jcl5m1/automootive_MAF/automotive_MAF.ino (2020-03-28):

// originally written by Johnny Lee <jcl5m1+ventilator@gmail.com>

//some variables to tweek
#define version "20200322.0"
#define led_pin 13
#define flow_pin A0
#define button_pin 2
#define serial_baud 9600

#define zero_flow_samples 100

int buttonState = 1;
int buttonStatePrev = 1;
int raw_flow = 0;
int loop_count = 0;
float zero_flow = 0;
float flow_estimate = 0;
float volume_estimate = 0;
int loop_counter_start = 0;
void setup() {

  Serial.begin(serial_baud);
  Serial.print("Version:\t");
  Serial.println(version);

  pinMode(led_pin, OUTPUT);
  pinMode(flow_pin, INPUT);
  pinMode(button_pin, INPUT_PULLUP);
  digitalWrite(led_pin, HIGH);

  Serial.print("Sampling zero flow...");

  for(int i =0 ; i < zero_flow_samples; i++){
    zero_flow += analogRead(flow_pin);
  }
  zero_flow /= zero_flow_samples;
  Serial.println("Done");
  
}

void loop() {

  buttonStatePrev = buttonState;
  buttonState = digitalRead(button_pin);
  
  if(buttonState == 0){
    // due to drift, and 1 way flow sensing.
    // on expiration - zero volume estimate, and re-estimate zero_flow
    volume_estimate = 0;
    if(buttonStatePrev == 1){
      Serial.print("exp start");
      loop_counter_start = loop_count;
      zero_flow = 0;
    }
    zero_flow += analogRead(flow_pin);
  } else {
    // on inspiration start, finalize zero_flow estimate
    if(buttonStatePrev == 0){
      Serial.print("insp start");
      zero_flow /= loop_count - loop_counter_start;
    }

    loop_counter_start = 0;
    // for debugging breathing back pressure sensing
    flow_estimate = analogRead(flow_pin) - zero_flow;
    volume_estimate += flow_estimate;
  }

  Serial.print(flow_estimate*20);
  Serial.print(",");
  Serial.println(volume_estimate);
  
  loop_count += 1;
  delay(10);  // approximately 100 cycles per second
}

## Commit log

2020-03-16 added first 3d model of mouthgaurd
    [mouthgaurd_v20200316.0.stl]
2020-03-16 mouth guard images and model
    [mouthgaurd_v20200316.0.stl, mouthgaurd_v20200316.1.stl]
2020-03-17 added 3D models for filter adapters
    [3M_filter_adapter.stl, NATO_40mm_adapter.stl]
2020-03-17 added images of filters
2020-03-17 modified to work with Arduino Nano vs Teensy 2.0++. Lowered maximum pressure to be around 20cm/H20.
2020-03-18 added sample data for detecting breathing back pressure did some pressure calibration and reduced highest pressure setting to around 20cm/H20
    [bipap_spd120_breathing_async.csv, bipap_spd120_breathing_sync.csv, bipap_spd120_open.csv, bipap_spd60_breathing_async.csv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]
2020-03-18 add image for current sensing
2020-03-20 Update README.md
    "But in order to get a good air seal to get enough positive pressure, this would require some tape. A little bit of leakage is actually desirable to allow CO2 to escape near the mouth nose and flushe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
    --> using a semi colon.
2020-03-21 Arduino-based Ventilator
    [PressureCoupling1_0.scad, PressureCoupling1_0.stl]
2020-03-21 Hose Adapter for MS3611 Pressure Sensor
    [MS3611PressureCoupling1_0.scad, MS3611PressureCoupling1_0.stl]
2020-03-25 MS6211 pressure log with 3M mask
    Log of several minutes of breathing. 98 kg male aged 60 at rest.
2020-03-26 Add .csv version of 3MmaskBreathPressureInvo
    .csv conversion of existing tab-delimited file
    [3MmaskBreathPressureInfo.csv]
2020-03-29 fixed bug in runtime printout
2020-03-30 added text code for sensirion3200 flow sensor
2020-03-30 disabled internal pullups on I2C line to enable 5v and 3.3v devices on same bus.
2020-03-30 added ms5611 cmh2o reading sample
2020-03-30 experimental integration of menu, pressure, and flow sensor. i2C is too slow for sensors and display
2020-03-30 Add files via upload
    CAD for Universal Inline Bacterial Viral Filter for CPAP Machines
    [Inline_filter_VB-65mm.STEP]
2020-04-03 AG Inductries Generic CPAP outlet filter CAD model draft
    [CPAP_outlet_filter_Lower_part.stl, CPAP_outlet_filter_Upper_part.stl, ventilator_filter_CPAP.f3d]
2020-04-03 CPAM ventilator based on real model
    [CPAP_outlet_filter_Lower_part.stl, CPAP_outlet_filter_Upper_part.stl, ventilator_filter_CPAP.f3d]
2020-04-04 Adjustments to the models after 3D-printing test
    [CPAP_outlet_filter_Lower_part.stl, CPAP_outlet_filter_Upper_part.stl, ventilator_filter_CPAP.f3d]
2020-04-04 Added description and photos of 3D printed model
2020-04-04 Move filter description to dedicated Wiki page
2020-04-17 Delete Filter_Testing_Sheet.png
    need to quote "kn95"
2020-04-17 Delete Filter_Testing_Sheet.png
    didn't seem to update
    trying to upload again
2020-04-17 Delete Filter_Testing_Sheet.png
    not updating
